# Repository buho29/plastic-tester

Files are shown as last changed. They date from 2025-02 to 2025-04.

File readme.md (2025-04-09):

# Plastic Tester

[Documentacion en español](<readme es.md>)

**Demo on YouTube**

Demo on YouTube (https://www.youtube.com/watch?v=grObh11XFaI)

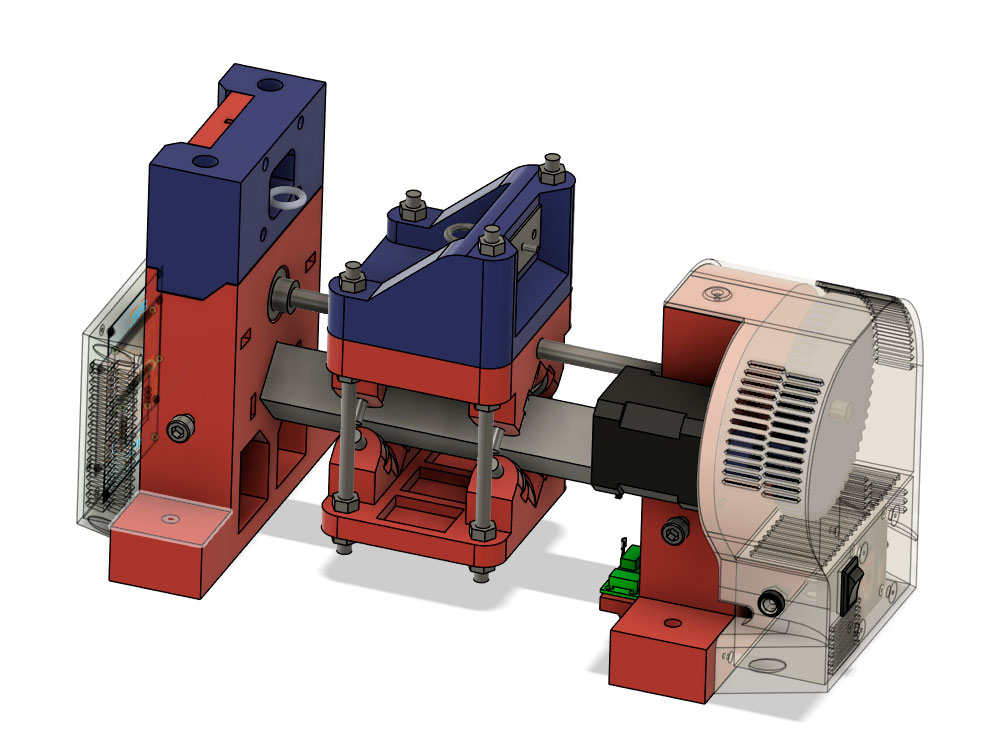
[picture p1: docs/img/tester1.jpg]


## General Description

Low-cost DIY system designed to perform tensile tests (*tensile testing machine*) on 3D-printed specimens.

Designed for:

- Validating the quality of 3D printing filaments
- Evaluating layer adhesion in printed parts
- Obtaining comparative data between different filaments
- Obtaining comparative data between different printing parameters
- Being compact and portable

The system uses:
- **Sensor**: Affordable load cell with HX711
- **Actuator**: Stepper motor with driver
- **Control**: Web interface accessible via WiFi
- **Visualization**: Real-time force/displacement graphs

**Key Features**:
- Approximate cost: < €100 in components
- Maximum force: 50kg
- Accuracy: ±0.1kg
- Adjustable speed: 0.1 - 5 mm/min

## Development Notes
- Platform: ESP32
- IDE: PlatformIO

## 3D Printing
- The printable parts and original files (Fusion 360) are located in the folder
[docs/3d](./docs/3d)

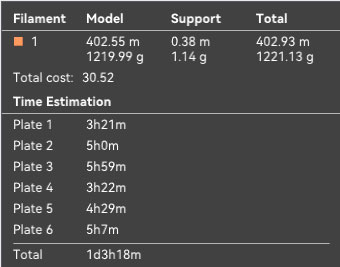
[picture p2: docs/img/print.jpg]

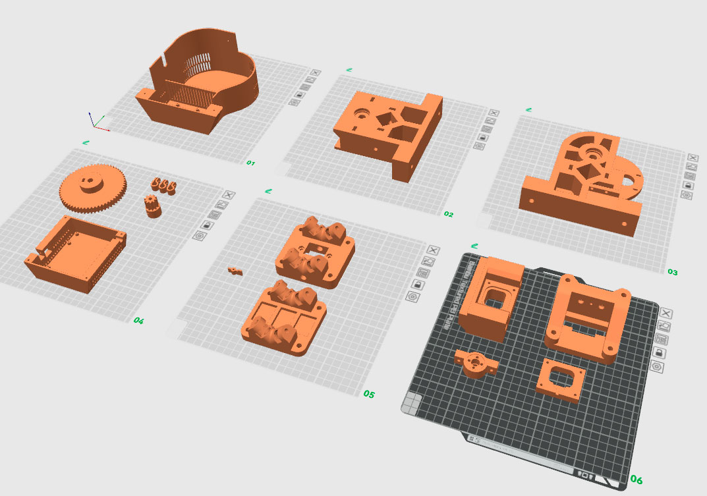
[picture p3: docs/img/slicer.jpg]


## Assembly
### Frame
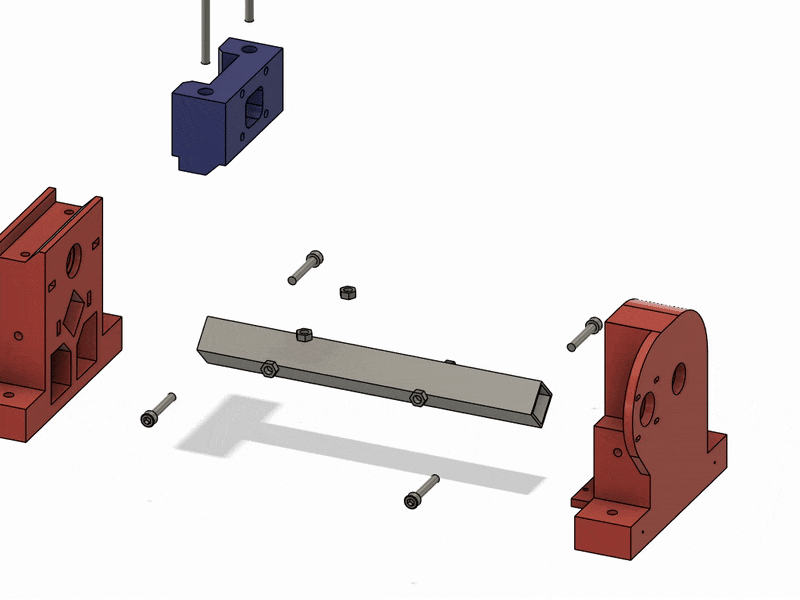
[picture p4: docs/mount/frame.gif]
Frame


[Download video](./docs/mount/frame.avi)

### Mount the T8 nut on the holder with inserts

- Cut off the excess screws

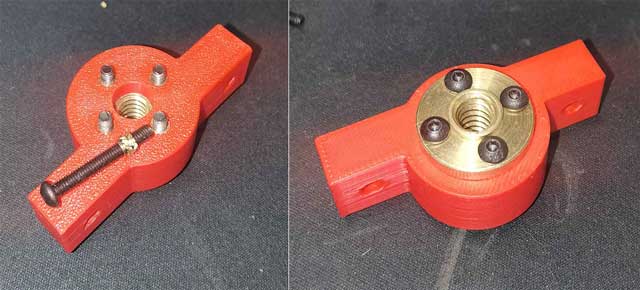
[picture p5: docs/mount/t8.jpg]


### Slide
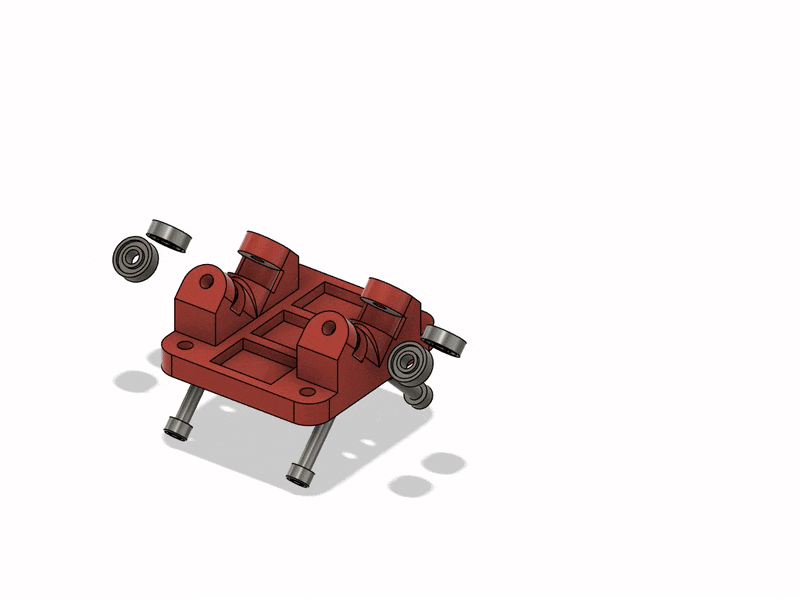
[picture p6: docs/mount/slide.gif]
slide


[Download video](./docs/mount/slide.avi)

### Complete
slide

[Download video](./docs/mount/mount.avi)

### Aligning the T8 nut holder with the lead screw

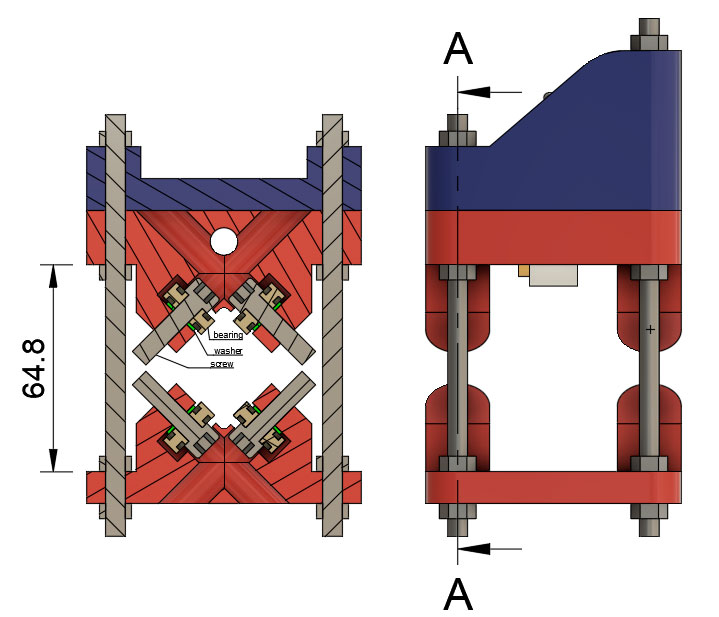
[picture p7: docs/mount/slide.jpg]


The screw is 5.8mm in diameter, and the bearings have a 6mm inner diameter.

1. Best method:
    - Center the screw with electrical tape.
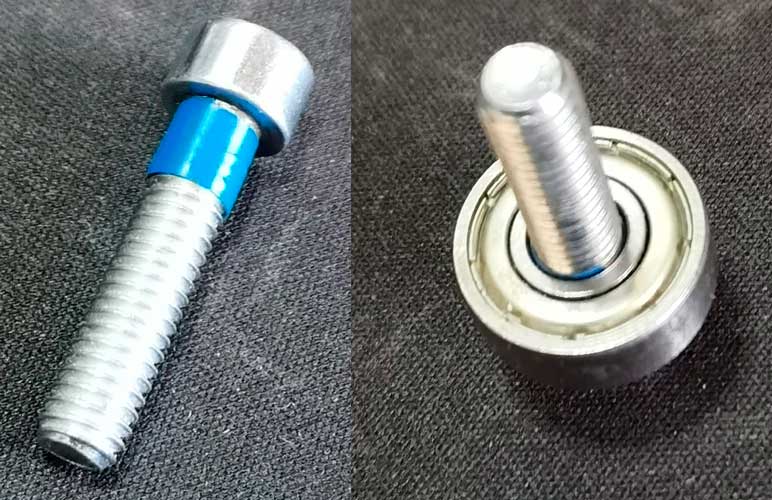
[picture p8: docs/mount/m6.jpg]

    - Place 2 pieces of 0.2mm paper; since the support area has a base, I left 0.25mm of clearance.
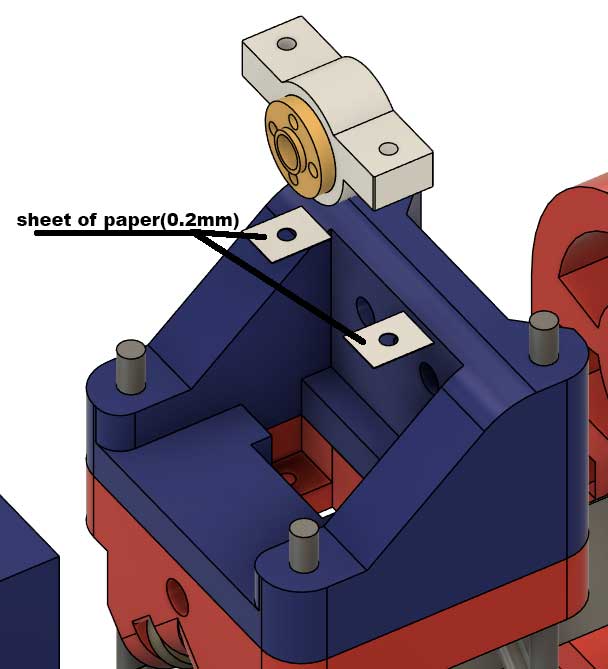
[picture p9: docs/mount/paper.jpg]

2. Alternative method:
    - Push towards the base and tighten the screw.
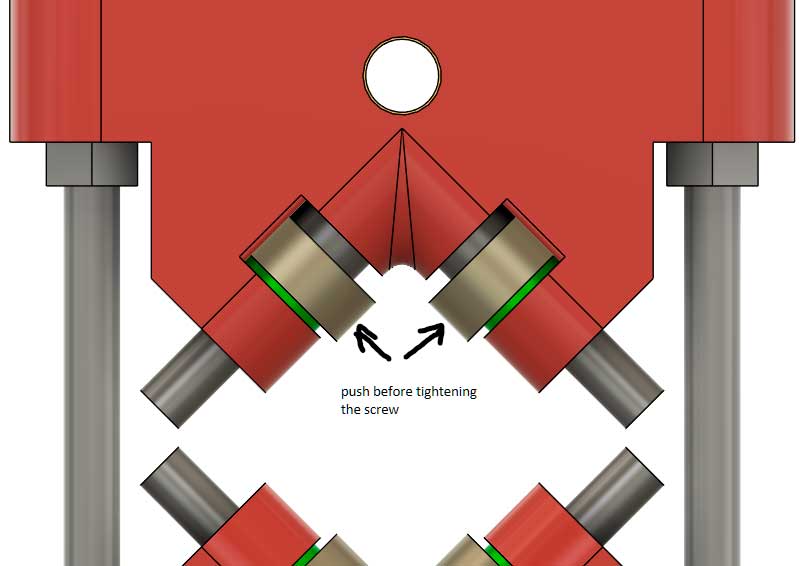
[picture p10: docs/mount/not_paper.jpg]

    - Place 4 or more pieces of 0.2mm paper.

## Hardware

### Load Cell (HX711)
```cpp
const int LOADCELL_DOUT_PIN = 26;
const int LOADCELL_SCK_PIN = 25;
const float CALIBRATING_FACTOR = -2316138 / 44.34; // real kg reading
```
1. **Set the HX711 to 80hz** 
    - Cut the blue square
    - Solder the red square 

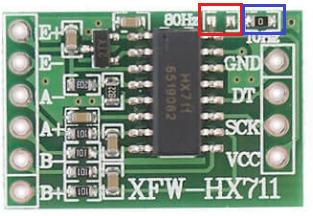
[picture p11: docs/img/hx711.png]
hx711


2. **Attach the screw to the sensor**
    - Drill with a 3mm bit 
    - Attach the eye screw with 2 nuts

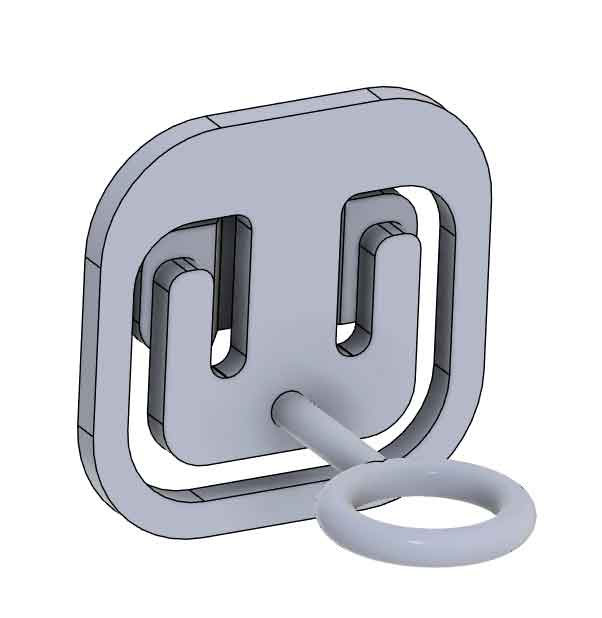
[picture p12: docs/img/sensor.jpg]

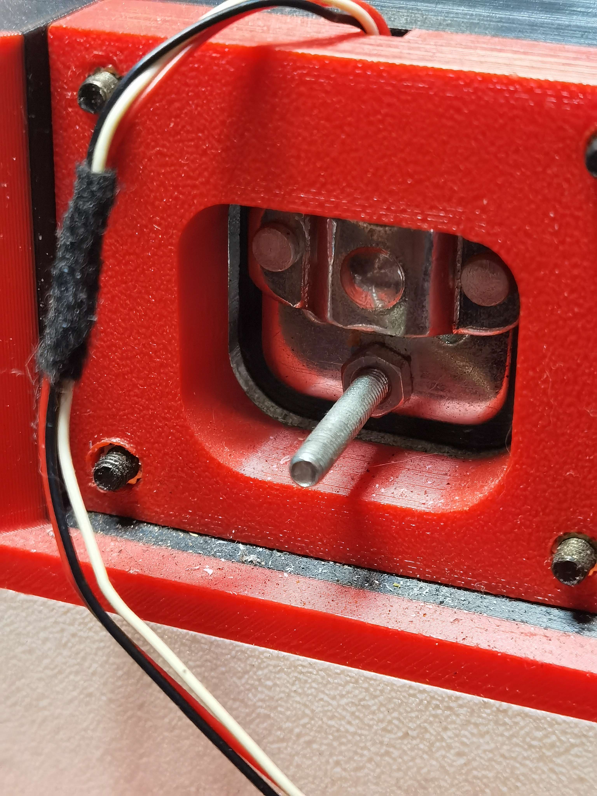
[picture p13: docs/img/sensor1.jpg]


**Note: The screw must be soldered**
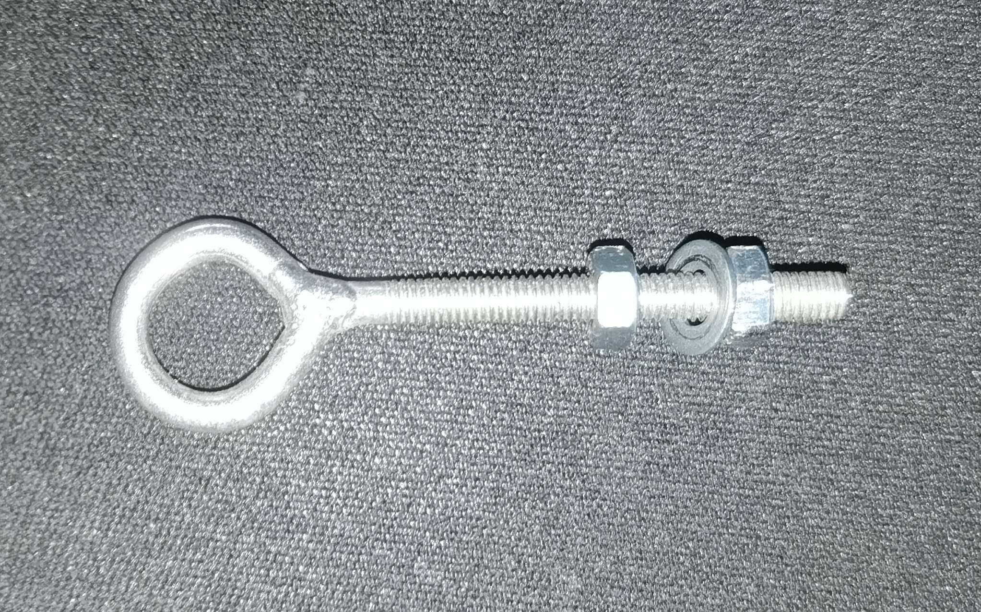
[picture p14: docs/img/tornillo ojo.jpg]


### PCB
 - 2 resistors of 1K Ohm are needed
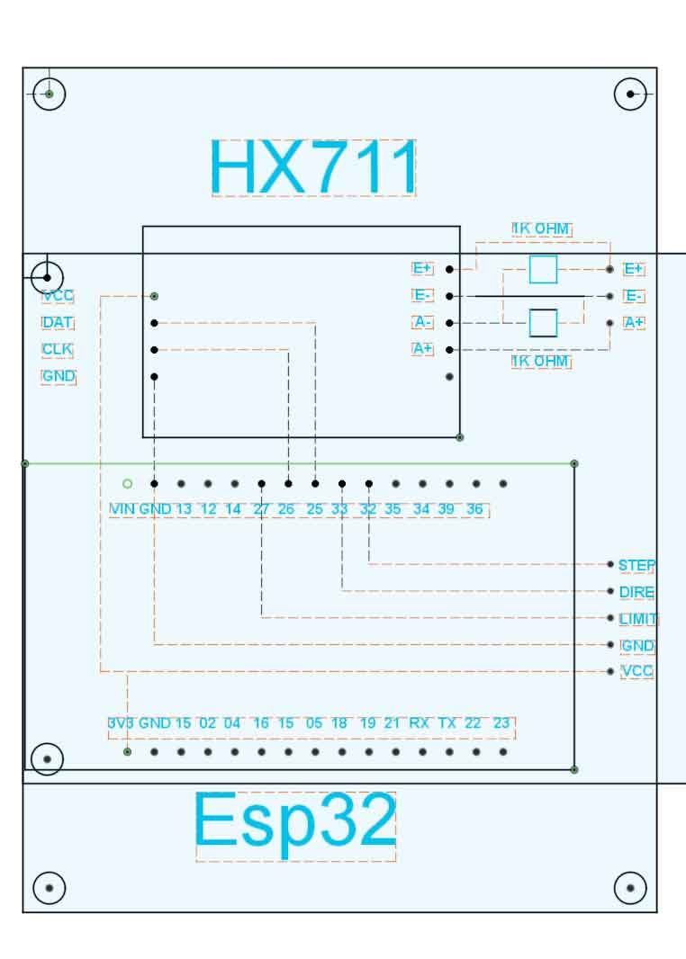
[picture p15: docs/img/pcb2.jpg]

**Flipped view (if looking from above)**
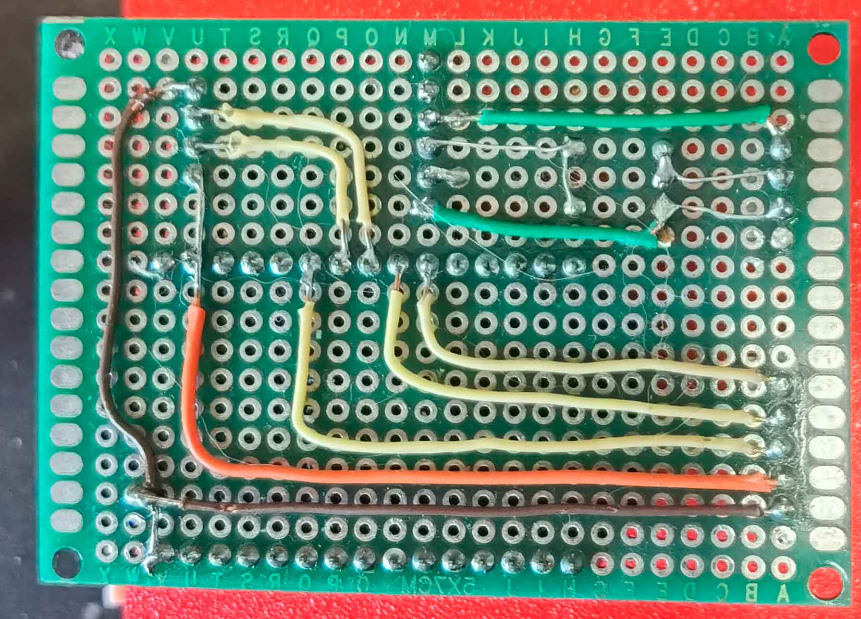
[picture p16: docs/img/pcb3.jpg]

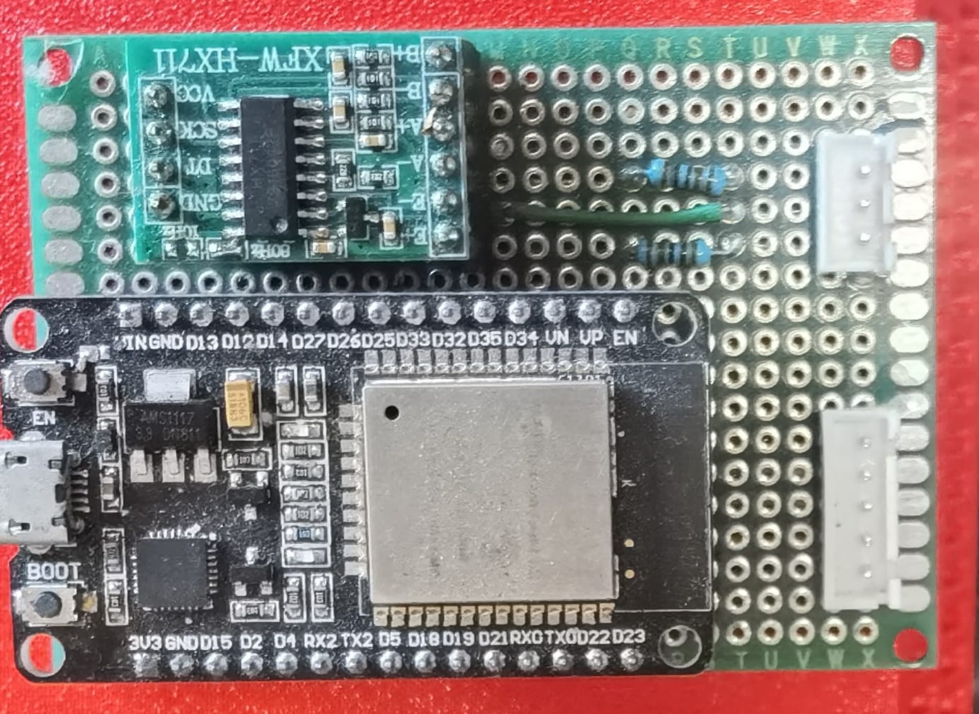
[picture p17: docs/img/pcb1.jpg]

**Normal view (if looking from below)**
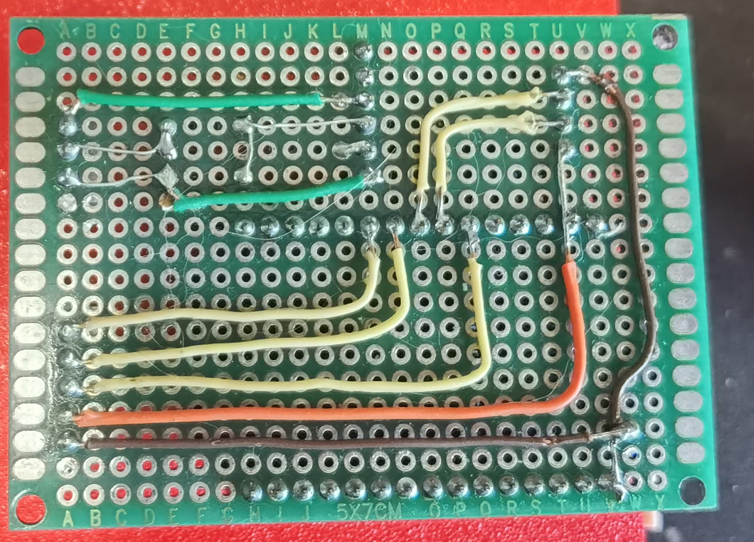
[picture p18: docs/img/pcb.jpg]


### Complete Circuit
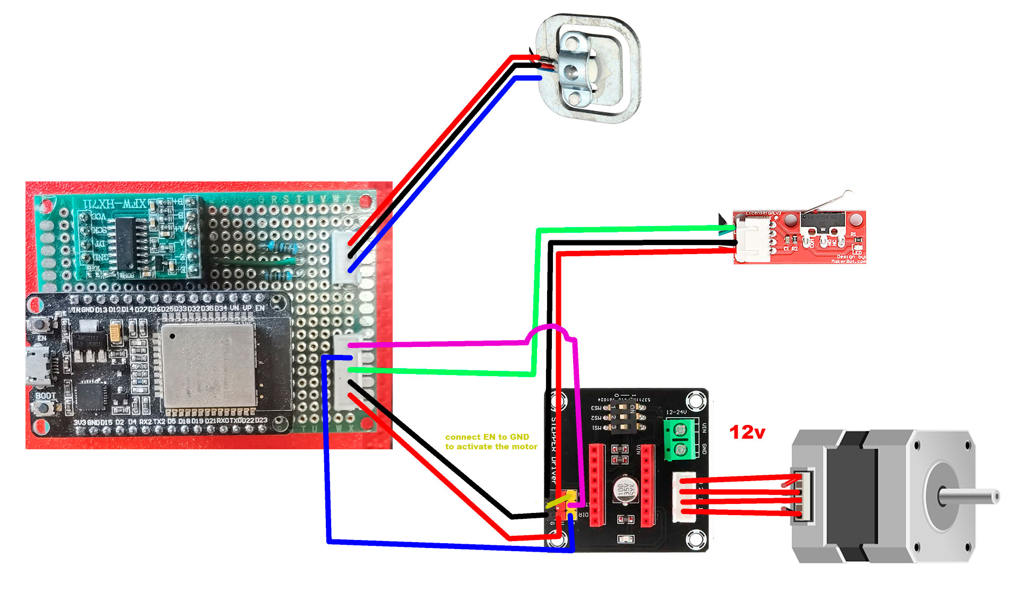
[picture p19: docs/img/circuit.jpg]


### Stepper Motor
```cpp
const uint8_t MOTOR_STEP_PIN = 32;
const uint8_t MOTOR_DIRECTION_PIN = 33;
const uint8_t ENDSTOP_PIN = 27;
```
## Installation

1. **Edit [config.json](./data/data/config.json): (optional)**
    ```json
    {
      "wifi_pass": "your pass",
      "wifi_ssid": "your wifi"
    }
    ```
2. **Upload the `data` folder to the ESP32:**
    1. If you want to update/copy the `vue` folder to `data/www`, run:
        ```bash
        python update_data_web.py 
        ```
    2. Steps in PlatformIO:
        - Build filesystem image
        - Upload filesystem image
3. **Compile the project:**
    1. Upload

## Usage

By default, the user is:
- **Username**: admin
- **Password**: admin

### On PC
- Open the browser and go to [http://plastester.local](http://plastester.local)
- Change the WiFi credentials if necessary (Options Page)

### On Mobile (Android)
mDNS does not work on mobile devices, you need to use the IP:
- If connected to WiFi, open the browser and go to your device's IP (e.g., [http://192.168.1.57](http://192.168.1.57))
- If not connected or you don't know the IP:
    - Connect to the device's WiFi and open the browser at [http://plastester.local](http://plastester.local) or [http://8.8.4.4](http://8.8.4.4)
    - Copy the IP and change the WiFi credentials if necessary (System/Options Page)

### Open from `index.html` in the `vue` folder
- Edit the `index.html` and change the host by setting the ESP32's IP:
    ```js
    // To run the HTML outside the ESP32 
    var host = document.location.host;
    if (host === "" || // local file
        host === "127.0.0.1:3000") // preview in preview (visual code addon)
        host = '192.168.1.57'; // ESP32 IP
    ```

## Vue/Quasar

- Using **Vue v2** and **Quasar v1** (decided not to upgrade to Vue 3 for now)
- Not using CLI, editing `.js` files directly in the `vue` folder

## Web Page Files
- `index.html`: Home and host configuration and web colors
- `main.js`: Router and Vue creation and configuration
- `vuex.js`: WebSocket data and event management
- `pages/`: Folder containing the web pages
- `components.js`: Definition of components used on the web (charts)

## Shopping List

**The links are for reference only, make sure it's the best purchase** 

| Item                              | Used | (€)  | Link |
|----------------------------------|------|------|------|
| **Main Components**              |      |      |      |
| Screw Trapezoidal T8 300mm P2L2  | 1    | 9,89 | [Link](https://es.aliexpress.com/item/32507277503.html) |
| Nema17 48mm 2A                   | 1    | 13,19| [Link](https://es.aliexpress.com/item/1005004731197516.html) |
| Stepper DRV8825                  | 1    | 1,59 | [Link](https://www.aliexpress.com/item/4000083334758.html) |
| Expansion Board Stepper          | 1    | 1,79 | [Link](https://es.aliexpress.com/item/10000278156894.html) |
| Weight Sensor 50KG               | 1    | 1,30 | [Link](https://es.aliexpress.com/item/1005006668822214.html) |
| HX711 Green Small                | 1    | 1,18 | [Link](https://www.aliexpress.com/item/1005007091731394.html) |
| ESP32 DEVKIT V1                  | 1    | 3,79 | [Link](https://es.aliexpress.com/item/1005008503831020.html) |
| F8-22M Bearing Axial 8x22x7 (x2) | 2    | 1,89 | [Link](https://es.aliexpress.com/item/1005007129279401.html) |
| 606ZZ 6x17x6mm (x10)             | 8    | 3,09 | [Link](https://es.aliexpress.com/item/1005003067718206.html) |
| 608zz 8x22x7mm (x10)             | 2    | 3,89 | [Link](https://es.aliexpress.com/item/1005003067718206.html) |
| Square Alu 25x25x2 - 250         | 1    | 3,59 | [Link](https://es.aliexpress.com/item/1005007456875848.html) |
| Endstop Switch                   | 1    | 2,79 | [Link](https://es.aliexpress.com/item/1005003139255707.html) |
| Lock Collar T8 (x5)              | 3    | 1,69 | [Link](https://es.aliexpress.com/item/1005001667273798.html) |
| Power Supply Jack Socket         | 1    | 0,54 | [Link](https://www.aliexpress.com/item/32838214586.html) |
| Switch (x5)                      | 1    | 1,34 | [Link](https://www.aliexpress.com/item/32873386670.html) |
| XH2.54 Connector                 | 1    | 2,99 | [Link](https://www.aliexpress.com/item/1005007425641197.html) |
| M3xL3xOD4.2 (x50)                | 10   | 1,59 | [Link](https://www.aliexpress.com/item/1005006472702418.html) |
| PCB Board Protoboard 5x7         | 1    | 0,90 | [Link](https://www.aliexpress.com/item/1005006100148769.html) |
| 1K Ohm resistor                  | 2    |      |      |
| **Total Components**             |      | 57,03|      |
|                                  |      |      |      |
| **Screws and Accessories (best in local seller)**       |      |      |      |
| D Ring Shackle Closed M3 (x2)    | 2    | 2,82 | [Link](https://www.aliexpress.com/item/1005007576884635.html) |
| Nuts M6 (x50)                    | 28   | 4,28 | [Link](https://www.aliexpress.com/item/1005007593861199.html) |
| Nuts M4 (x25)                    | 2    | 1,59 | [Link](https://www.aliexpress.com/item/1005007593861199.html) |
| Nuts M3 (x50)                    | 8    | 1,69 | [Link](https://es.aliexpress.com/item/1005004531602992.html) |
| Screw M6 X 25 (x20)              | 12   | 5,84 | [Link](https://www.aliexpress.com/item/1005003463456440.html) |
| Screw M6 X 60 (x10)              | 6    | 4,48 | [Link](https://www.aliexpress.com/item/1005004527586307.html) |
| Screw M6 X 35 (x5)               | 4    | 1,89 | [Link](https://www.aliexpress.com/item/1005004527586307.html) |
| Screw M3 X 22 (x40)              | 8    | 2,05 | [Link](https://www.aliexpress.com/item/1005004527586307.html) |
| Screw M4 X 20 (x20)              | 2    | 1,95 | [Link](https://www.aliexpress.com/item/1005004527586307.html) |
| Washer M6 12x1.5 (x50)           | 8    | 2,06  | [Link](https://www.aliexpress.com/item/1005004527586307.html) |
| Sheep Eye Screw M3 (x10)         | 2    | 2,59 | Local Seller |
| Threaded Rod M6 -1000            | 1    | 0,80 | Local Seller |
| Plywood Board 340x160x20         | 1    | 6,00 | Local Seller |
| **Total Screws**                 |      | 38,04|      |
| **TOTAL GENERAL**                |      | 95,07|      |
|                                  |      |      |      |
| **Tools**                        |      |      |      |
| Crimping Plier XH2.54            | 1    | 9,39 | [Link](https://www.aliexpress.com/item/1005006224244342.html) |

## Libraries Used

### C++

- [ESPAsyncWebServer](https://github.com/ESP32Async/ESPAsyncWebServer)
- [AsyncTCP](https://github.com/ESP32Async/AsyncTCP)
- [ArduinoJson](https://arduinojson.org/)
- [FastAccelStepper](https://github.com/gin66/FastAccelStepper)

### JavaScript

- [Vue v2](https://v2.vuejs.org/)
- [Vuex v3](https://v3.vuex.vuejs.org/)
- [Vue-router v3](https://v3.router.vuejs.org/)
- [Quasar Framework v1](https://v1.quasar.dev/)
- [Chart.js v2](https://www.chartjs.org)/[Vue-chartjs v3](https://vue-chartjs.org)

## Screens
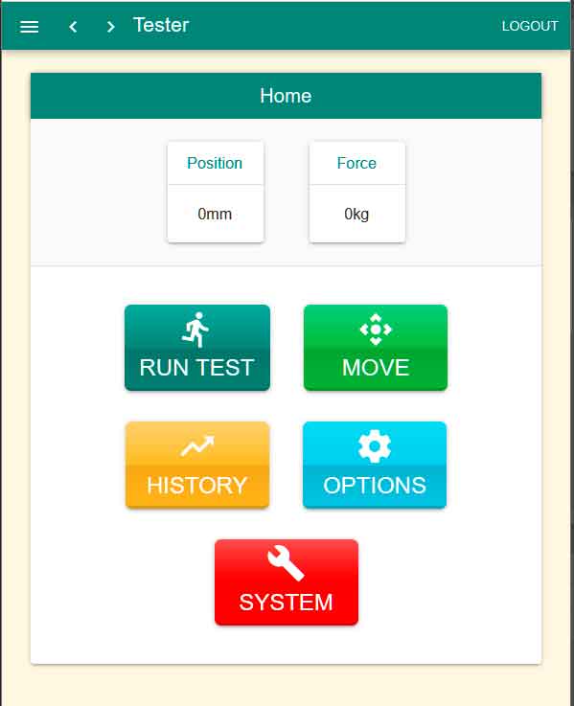
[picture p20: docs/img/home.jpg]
Home

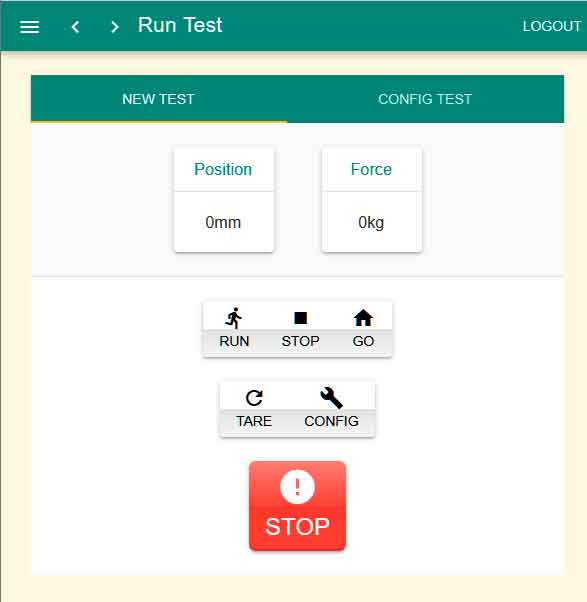
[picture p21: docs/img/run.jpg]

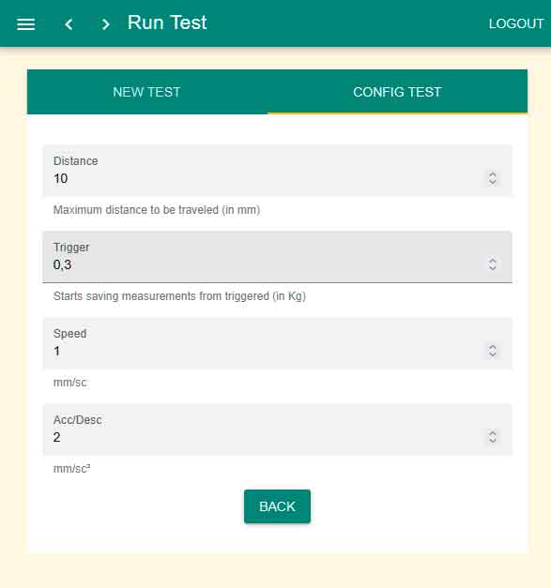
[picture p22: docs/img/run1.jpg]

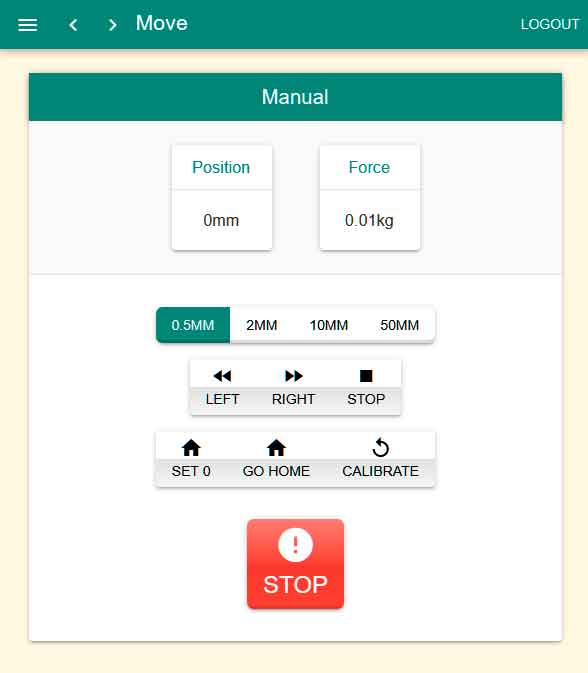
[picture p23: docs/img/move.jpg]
Move

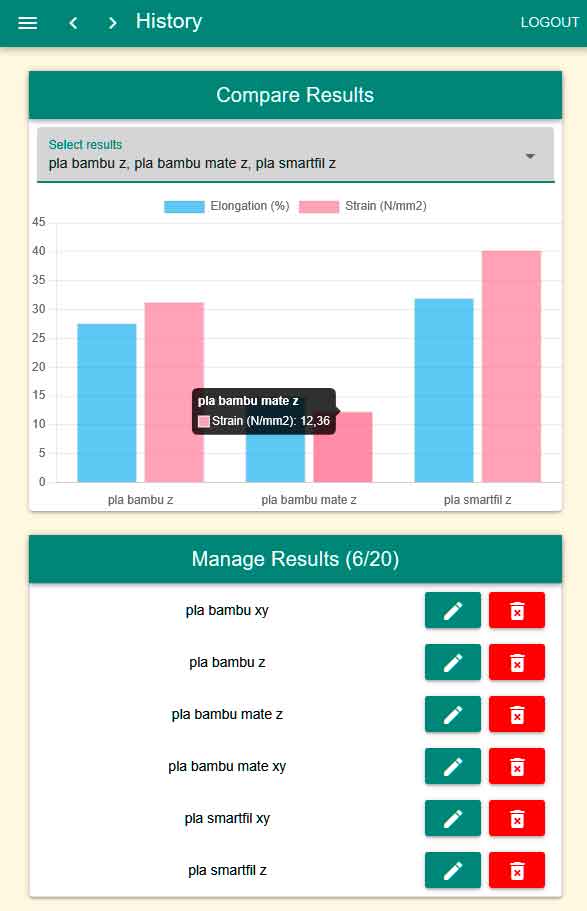
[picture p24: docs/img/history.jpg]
History

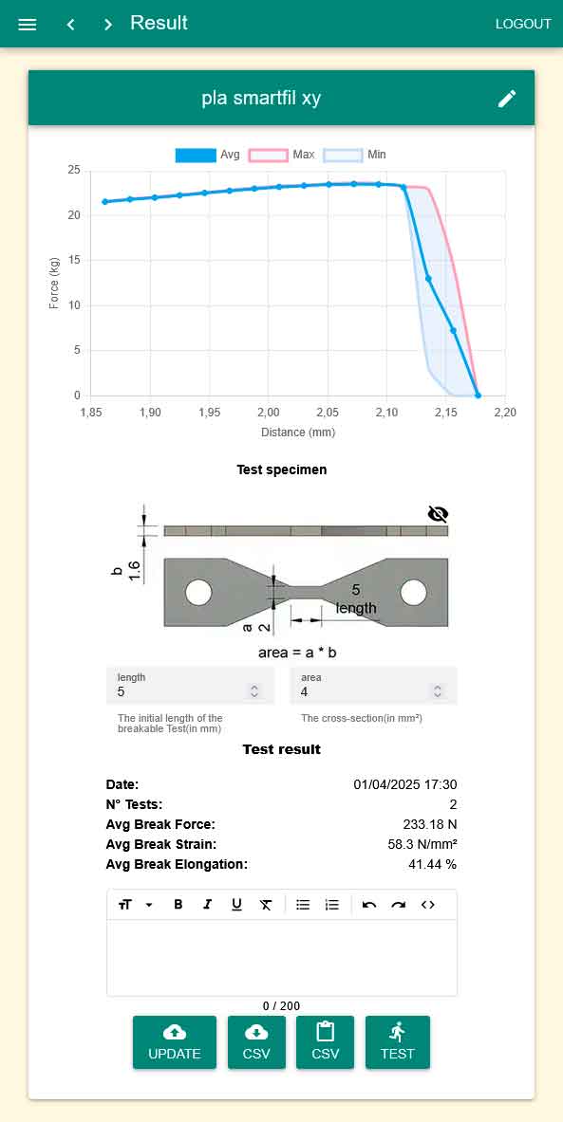
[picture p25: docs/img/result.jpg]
Result

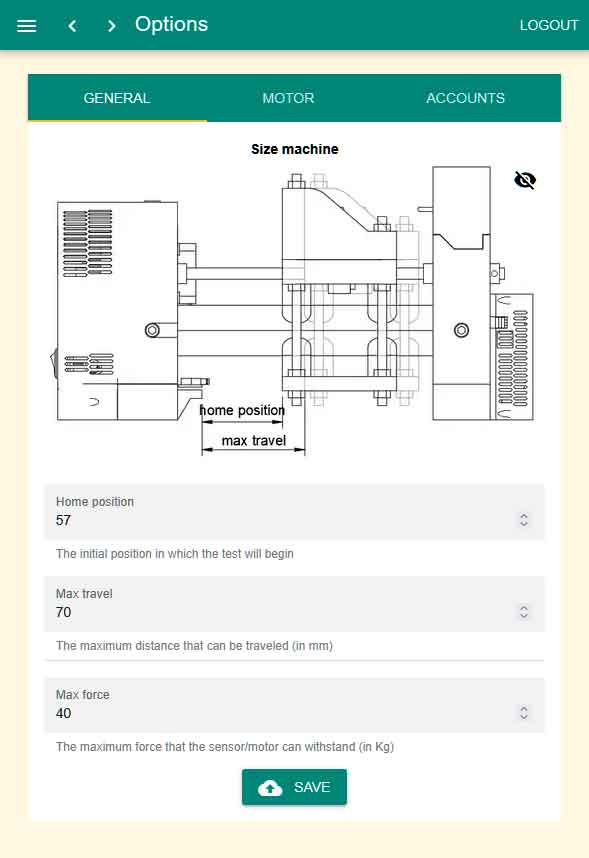
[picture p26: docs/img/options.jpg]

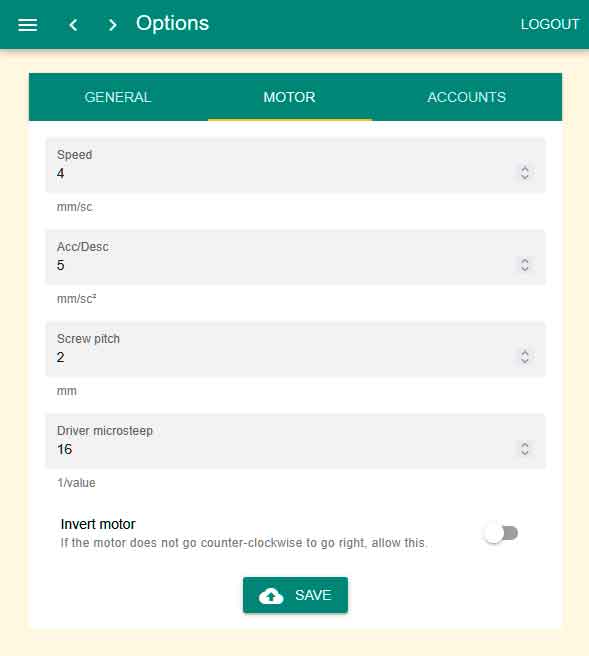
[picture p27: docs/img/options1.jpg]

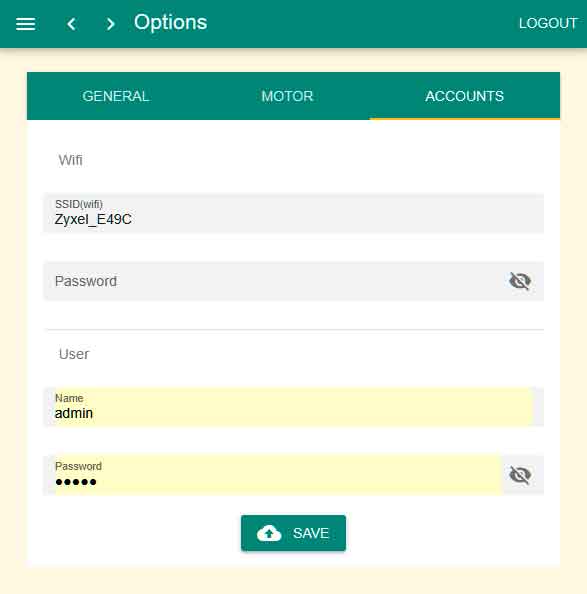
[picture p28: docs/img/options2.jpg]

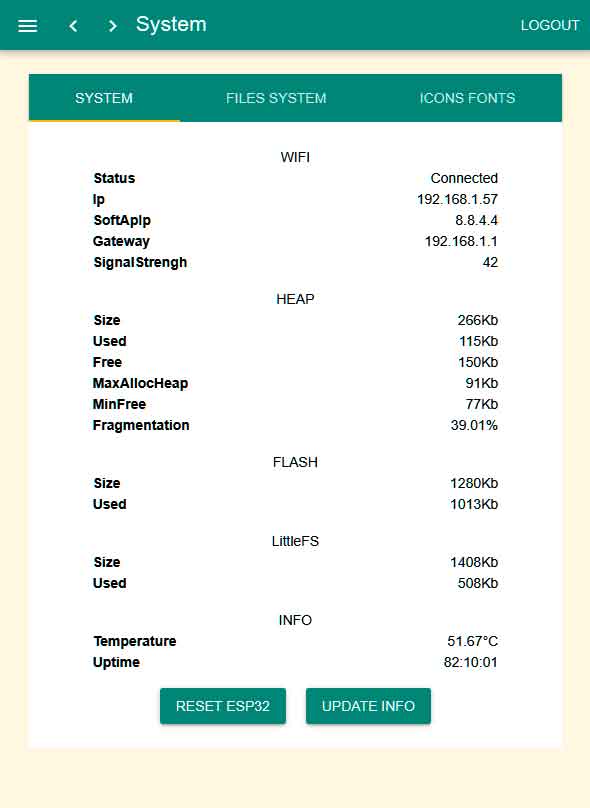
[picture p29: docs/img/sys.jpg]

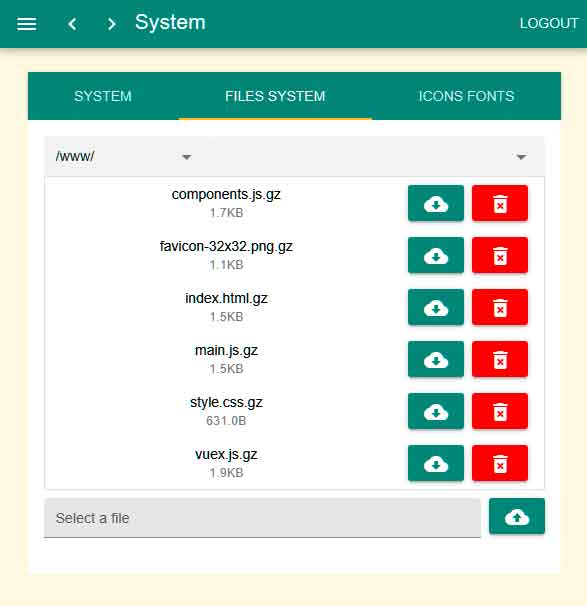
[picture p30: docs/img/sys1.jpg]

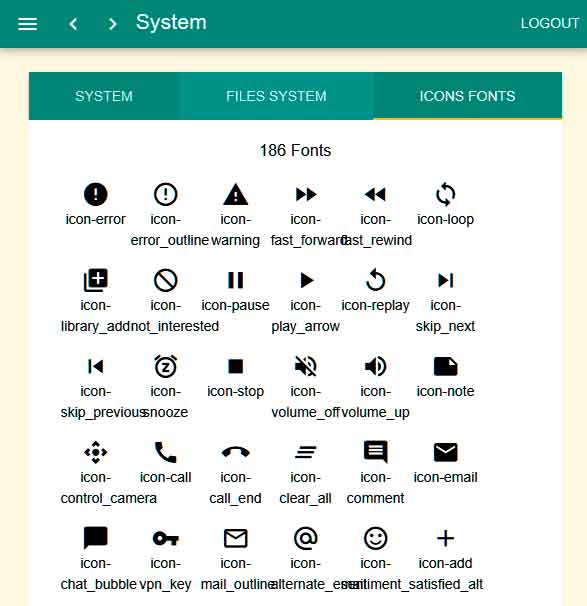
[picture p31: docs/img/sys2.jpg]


## Gallery
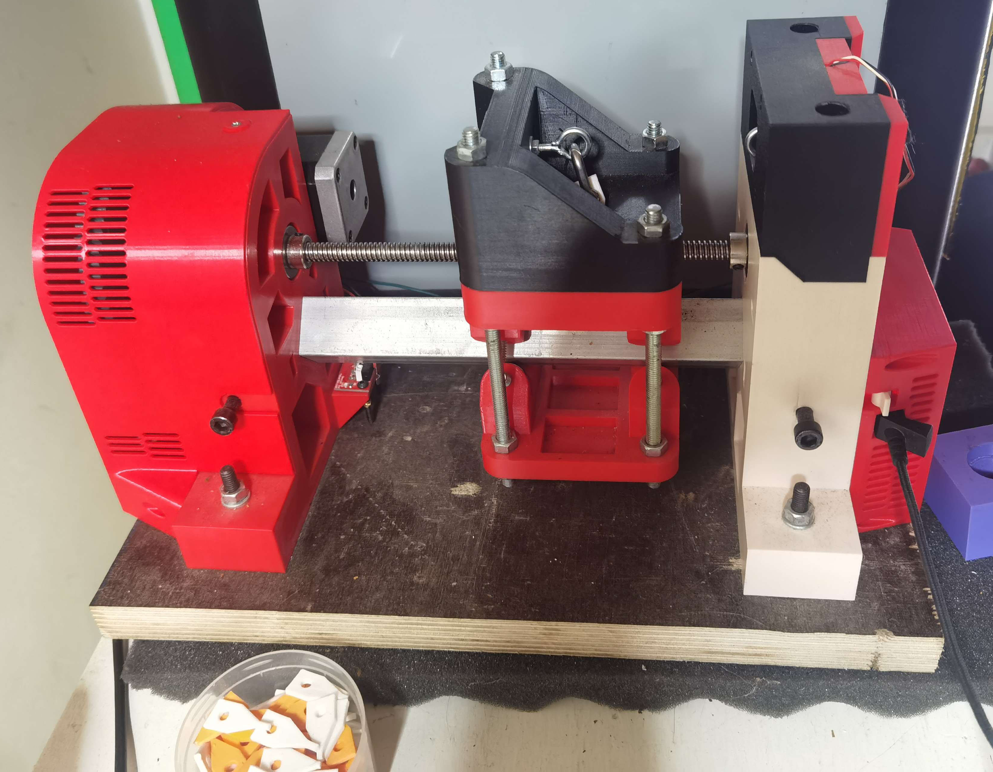
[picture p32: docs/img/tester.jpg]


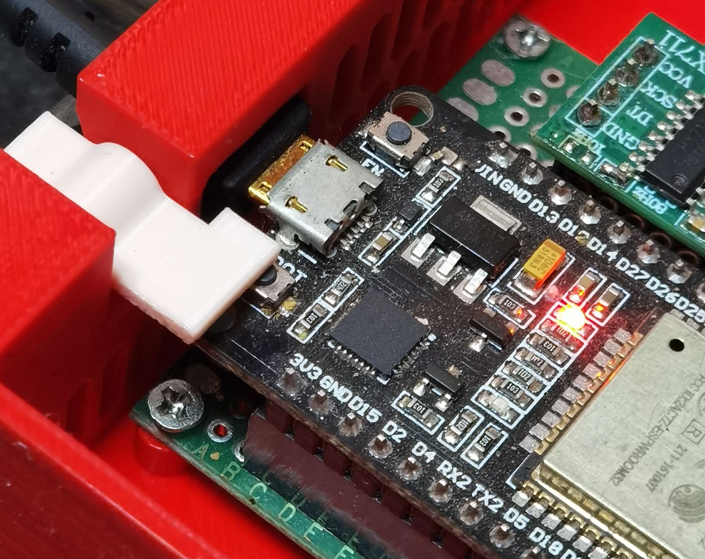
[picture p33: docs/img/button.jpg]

**I used a 2x13mm steel shaft** (a cut drill bit in my case)

- Insert it through the "usb" window

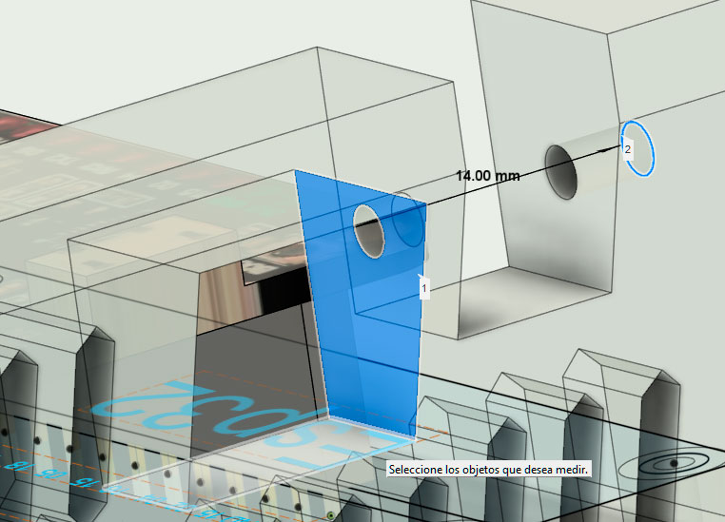
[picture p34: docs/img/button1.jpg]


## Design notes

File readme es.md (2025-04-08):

# Plastic Tester

**Demo en YouTube**

Demo en YouTube (https://www.youtube.com/watch?v=grObh11XFaI)



## Descripción General

Sistema DIY de bajo coste para realizar ensayos de tracción (*tensile testing machine*) en probetas impresas en 3D. 

Diseñado para:

- Validar la calidad de filamentos para impresión 3D
- Evaluar la adhesión entre capas de piezas impresas
- Obtener datos comparativos entre varios filamentos
- Obtener datos comparativos entre diferentes parámetros de impresión
- Que sea pequeño

El sistema utiliza:
- **Sensor**: Celda de carga económico con HX711
- **Actuador**: Motor paso a paso con driver
- **Control**: Interfaz web accesible vía WiFi
- **Visualización**: Gráficas de fuerza/desplazamiento

**Características principales**:
- Coste aproximado: < 100€ en componentes
- Fuerza máxima: 50kg
- Precisión: ±0.1kg
- Velocidad ajustable: 0.1 - 5 mm/min

## Notas de Desarrollo
- Plataforma: ESP32
- IDE: PlatformIO

## Impresion 3D
- las piezas para imprimir y los ficheros originales(fusion 360) se encuentran en la carpeta
[docs/3d](./docs/3d)




## Montaje
### Frame
Frame

[Descargar video](./docs/mount/frame.avi)

### Montar la tuerca T8 en el soporte con los inserts

- cortar los tornillos sobrantes



### Slide
slide

[Descargar video](./docs/mount/slide.avi)

### Completo
slide

[Descargar video](./docs/mount/mount.avi)

### Alineamiento de el soporte de la tuerca T8 con el husillo



el tornillo mide 5.8mm de diámetro y los rodamientos tienen 6mm de interior

1. mejor forma
    - centrando el tornillo con cinta aislante,

    - poner 2 trozos de papel de 0.2mm, como la zona donde apoya lleva soporte le deje 0.25mm de holgura 

2. también funciona
    - empujando hacia la base y apretando el tornillo

    - poner 4 trozos de papel o mas de 0.2mm

## Hardware

### Celda de Carga (HX711)
```cpp
const int LOADCELL_DOUT_PIN = 26;
const int LOADCELL_SCK_PIN = 25;
const float CALIBRATING_FACTOR = -2316138 / 44.34; // lectura/kg real
```
1. **Poner el HX711 a 80hz** 
    - cortar el cuadrado azul
    - soldar el cuadrado rojo 

hx711

2. **Colocar tornillo al sensor**
    - taladrar con una broca de 3mm 
    - poner el tornillo de ojo con 2 tuercas




**nota el tornillo tiene que estar soldado**


### PCB
 - se necesitan 2 resistencias de 1K Ohm

**vista volteada (si miramos desde arriba)**


**vista normal (si miramos por abajo)**


### Circuito completo


### Motor Paso a Paso
```cpp
const uint8_t MOTOR_STEP_PIN = 32;
const uint8_t MOTOR_DIRECTION_PIN = 33;
const uint8_t ENDSTOP_PIN = 27;
```
## Instalación

1. **Editar [config.json](./data/data/config.json): (opcional)**
    ```json
    {
      "wifi_pass": "tu pass",
      "wifi_ssid": "tu wifi"
    }
    ```
2. **Subir la carpeta `data` al ESP32:**
    1. Si deseas actualizar/copiar la carpeta `vue` a `data/www` ejecutar:
        ```bash
        python update_data_web.py 
        ```
    2. Pasos en PlatformIO:
        - Build filesystem image
        - Upload filesystem image
3. **Compilar el proyecto:**
    1. Upload

## Uso

Por defecto el usuario es:
- **Usuario**: admin
- **Password**: admin

### En PC
- Abre el navegador y ve a [http://plastester.local](http://plastester.local)
- Cambiar las credenciales del WiFi si es necesario (Pagina Options)

### En Móvil (Android)
El mDNS no funciona en móviles, necesitas usar la IP:
- Si está conectado al WiFi, abre el navegador y ve a la IP de tu dispositivo (ej.: [http://192.168.1.57](http://192.168.1.57))
- Si no está conectado o no sabes la IP:
    - Conéctate al WiFi del dispositivo y abre el navegador en [http://plastester.local](http://plastester.local) o [http://8.8.4.4](http://8.8.4.4)
    - Copia la IP y cambia las credenciales del WiFi si es necesario (Pagina System/Options)

### Abrir desde `index.html` de la carpeta `vue`
- Editar el `index.html` y cambiar el host poniendo la IP del ESP32:
    ```js
    // Para ejecutar el HTML fuera del ESP32 
    var host = document.location.host;
    if (host === "" || // archivo local
        host === "127.0.0.1:3000") // vista previa en preview (addon visual code)
        host = '192.168.1.57'; // IP del ESP32
    ```

## Vue/Quasar

- Uso **Vue v2** y **Quasar v1** (decidí no actualizar a Vue 3 por ahora)
- No uso CLI, edito los `.js` directamente de la carpeta `vue`

## Ficheros de la pagina web
- `index.html`: Inicio y configuración de host y colores de la web
- `main.js`: Creación y configuración de router y Vue
- `vuex.js`: Gestión de datos y eventos WebSocket
- `pages/`: Carpeta donde estan las páginas de la web
- `components.js`: Definición componentes usadas en la web (charts)

## Lista de la compra

**Los links solo son de referencia, asegurarse que es la mejor compra** 

| Item                             | Used | (€)  | Link |
|----------------------------------|------|------|------|
| **Componentes Principales**      |      |      |      |
| Screw Trapezoidal T8 300mm P2L2  | 1    | 9,89 | [Link](https://es.aliexpress.com/item/32507277503.html) |
| Nema17 48mm 2A                   | 1    | 13,19| [Link](https://es.aliexpress.com/item/1005004731197516.html) |
| Stepper DRV8825                  | 1    | 1,59 | [Link](https://www.aliexpress.com/item/4000083334758.html) |
| Expansion Board Stepper          | 1    | 1,79 | [Link](https://es.aliexpress.com/item/10000278156894.html) |
| Weight Sensor 50KG               | 1    | 1,30 | [Link](https://es.aliexpress.com/item/1005006668822214.html) |
| HX711 Green Small                | 1    | 1,18 | [Link](https://www.aliexpress.com/item/1005007091731394.html) |
| ESP32 DEVKIT V1                  | 1    | 3,79 | [Link](https://es.aliexpress.com/item/1005008503831020.html) |
| F8-22M Bearing Axial 8x22x7 (x2) | 2    | 1,89 | [Link](https://es.aliexpress.com/item/1005007129279401.html) |
| 606ZZ 6x17x6mm (x10)             | 8    | 3,09 | [Link](https://es.aliexpress.com/item/1005003067718206.html) |
| 608zz 8x22x7mm (x10)             | 2    | 3,89 | [Link](https://es.aliexpress.com/item/1005003067718206.html) |
| Square Alu 25x25x2 - 250         | 1    | 3,59 | [Link](https://es.aliexpress.com/item/1005007456875848.html) |
| Endstop Switch                   | 1    | 2,79 | [Link](https://es.aliexpress.com/item/1005003139255707.html) |
| Lock Collar T8 (x5)              | 3    | 1,69 | [Link](https://es.aliexpress.com/item/1005001667273798.html) |
| Power Supply Jack Socket         | 1    | 0,54 | [Link](https://www.aliexpress.com/item/32838214586.html) |
| Switch (x5)                      | 1    | 1,34 | [Link](https://www.aliexpress.com/item/32873386670.html) |
| XH2.54 Connector                 | 1    | 2,99 | [Link](https://www.aliexpress.com/item/1005007425641197.html) |
| M3xL3xOD4.2 (x50)                | 10   | 1,59 | [Link](https://www.aliexpress.com/item/1005006472702418.html) |
| PCB Board Protoboard 5x7         | 1    | 0,90 | [Link](https://www.aliexpress.com/item/1005006100148769.html) |
| 1K Ohm resistor                  | 2    |      |      |
| **Total Componentes**            |      | 57,03|      |
|                                  |      |      |      |
| **Tornillos y Accesorios (mejor de un vendedor local)** |      |      |      |
| D Ring Shackle Closed M3 (x2)    | 2    | 2,82 | [Link](https://www.aliexpress.com/item/1005007576884635.html) |
| Nuts M6 (x50)                    | 28   | 4,28 | [Link](https://www.aliexpress.com/item/1005007593861199.html) |
| Nuts M4 (x25)                    | 2    | 1,59 | [Link](https://www.aliexpress.com/item/1005007593861199.html) |
| Nuts M3 (x50)                    | 8    | 1,69 | [Link](https://es.aliexpress.com/item/1005004531602992.html) |
| Screw M6 X 25 (x20)              | 12   | 5,84 | [Link](https://www.aliexpress.com/item/1005003463456440.html) |
| Screw M6 X 60 (x10)              | 6    | 4,48 | [Link](https://www.aliexpress.com/item/1005004527586307.html) |
| Screw M6 X 35 (x5)               | 4    | 1,89 | [Link](https://www.aliexpress.com/item/1005004527586307.html) |
| Screw M3 X 22 (x40)              | 8    | 2,05 | [Link](https://www.aliexpress.com/item/1005004527586307.html) |
| Screw M4 X 20 (x20)              | 2    | 1,95 | [Link](https://www.aliexpress.com/item/1005004527586307.html) |
| Washer M6 12x1.5 (x50)           | 8    | 2,06  | [Link](https://www.aliexpress.com/item/1005004527586307.html) |
| Sheep Eye Screw M3 (x10)         | 2    | 2,59 | Local Seller |
| Threaded Rod M6 -1000            | 1    | 0,80 | Local Seller |
| Plywood Board 340x160x20         | 1    | 6,00 | Local Seller |
| **Total Tornillos**              |      | 38,04|      |
| **TOTAL GENERAL**                |      | 95,07|      |
|                                  |      |      |      |
| **Herramientas**                 |      |      |      |
| Crimping Plier XH2.54            | 1    | 9,39 | [Link](https://www.aliexpress.com/item/1005006224244342.html) |

## Librerías usadas

### C++

- [ESPAsyncWebServer](https://github.com/ESP32Async/ESPAsyncWebServer)
- [AsyncTCP](https://github.com/ESP32Async/AsyncTCP)
- [ArduinoJson](https://arduinojson.org/)
- [FastAccelStepper](https://github.com/gin66/FastAccelStepper)

### JavaScript

- [Vue v2](https://v2.vuejs.org/)
- [Vuex v3](https://v3.vuex.vuejs.org/)
- [Vue-router v3](https://v3.router.vuejs.org/)
- [Quasar Framework v1](https://v1.quasar.dev/)
- [Chart.js v2](https://www.chartjs.org)/[Vue-chartjs v3](https://vue-chartjs.org)

## Screens
Home
Run
Run
Move
History
Result
Icons
Icons
Icons
System
System
System

## Galeria



**he usado un eje de acero 2x13mm** (una broca cortada en mi caso)

- se mete por la ventana "usb"



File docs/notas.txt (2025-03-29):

opciones :
	+ guardar home position
	+ guardar inversion de motor
	+ guardar max distancia
	+ guardar max peso
	- probarlo

+ crear panel configuracion test (tab)
	+ distancia
	+ trigger 
- enums 
	- notify (good,warn)
	- action (empty,checklimit)
	- step test
	- wifiReset ()

+ revisar motor.setHome y setConfigHome
+ limitar comandos al stop cuando esta funcionado el test

- reseteo velocidad
[x] no se puede parar normal si esta en el test
[x] reseteo de velocidad si se para el test

A4988
VREF=Imax.8.Rs
Vref=1.5 *8*0.05 = 0.6v

DRV8825 
VREF=Imax/2
Vref= 1.5/2 = 0.75v

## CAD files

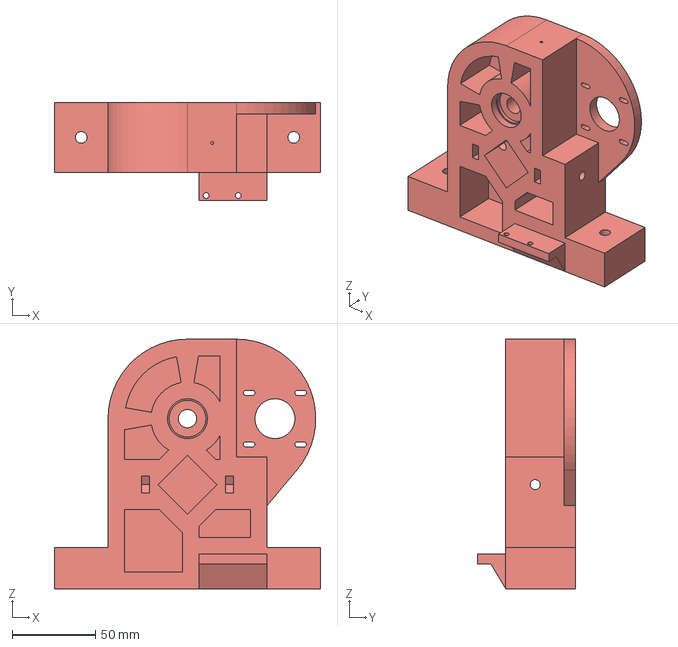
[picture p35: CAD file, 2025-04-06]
docs/3d/frame motor.step
160.0 x 59.0 x 150.2 mm

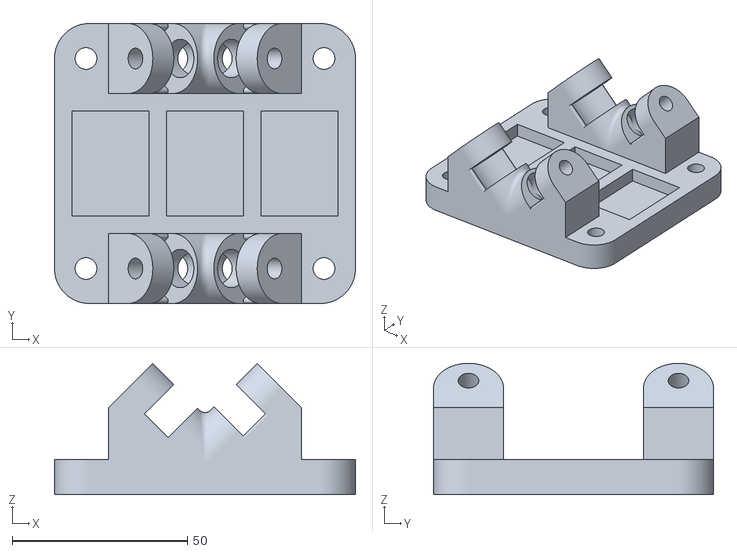
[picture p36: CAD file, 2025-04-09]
docs/3d/stl/slide-SOLID-2.stl
86.0 x 80.0 x 37.5

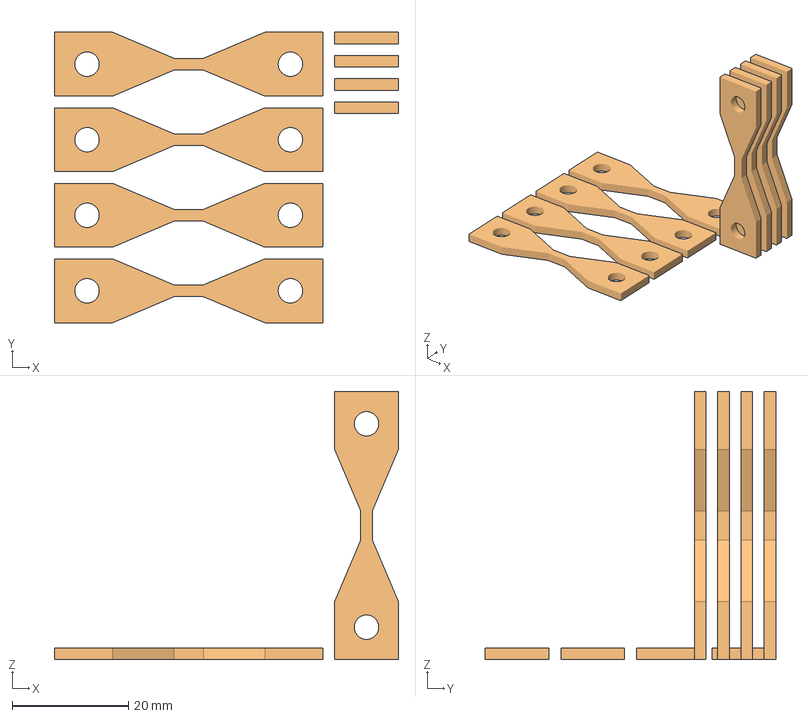
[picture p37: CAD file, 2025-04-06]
docs/3d/probeta.3mf
59.2 x 50.0 x 46.2 mm
Assembly x 2

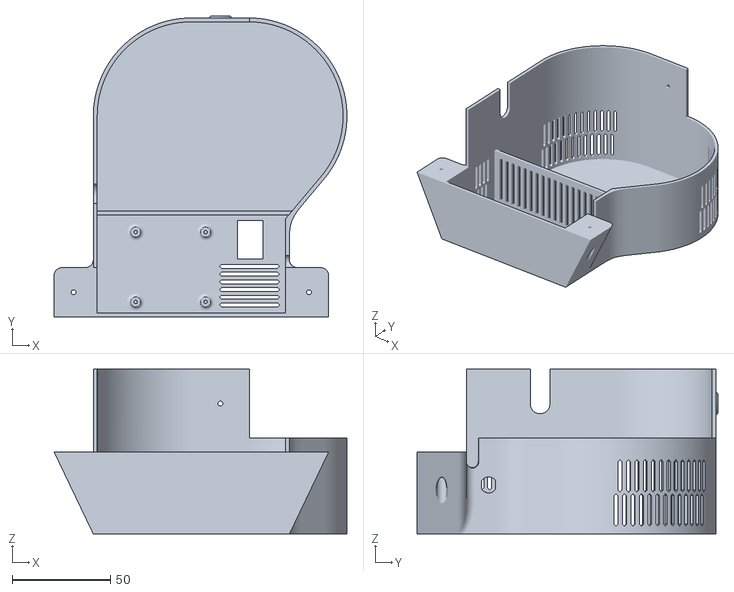
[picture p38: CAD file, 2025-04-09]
docs/3d/stl/tapa v2.stl
149.2 x 153.3 x 84.0

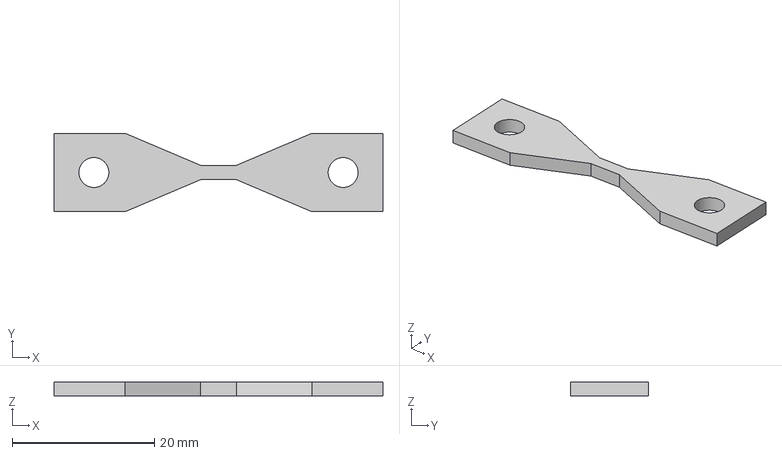
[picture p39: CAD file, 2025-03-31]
docs/3d/probeta v2.step
46.2 x 11.0 x 2.00 mm

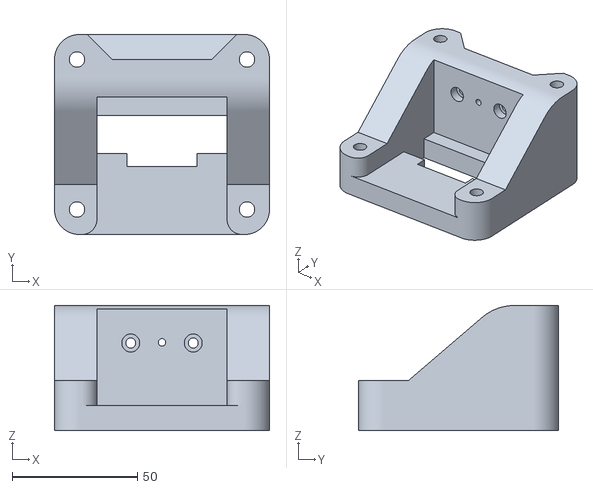
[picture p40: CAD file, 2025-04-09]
docs/3d/stl/COMPOUND-SOLID-4.stl
86.0 x 80.0 x 50.0

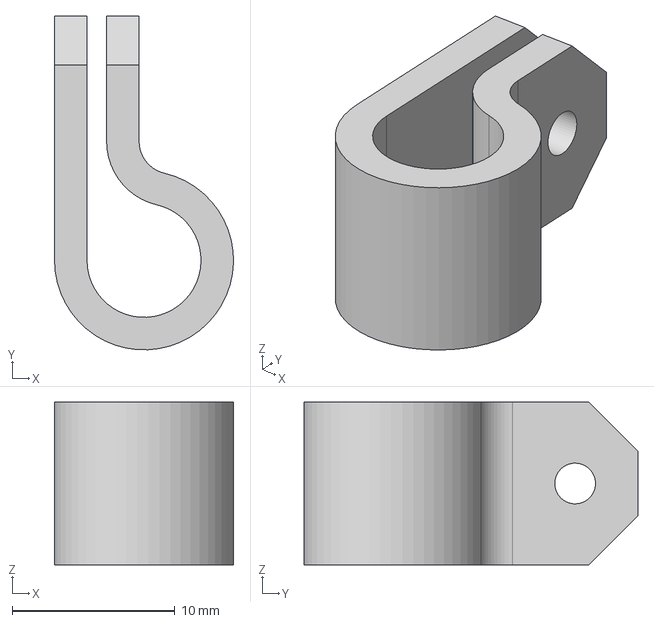
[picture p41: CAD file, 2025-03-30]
docs/3d/clip v1.step
11.0 x 20.5 x 10.0 mm

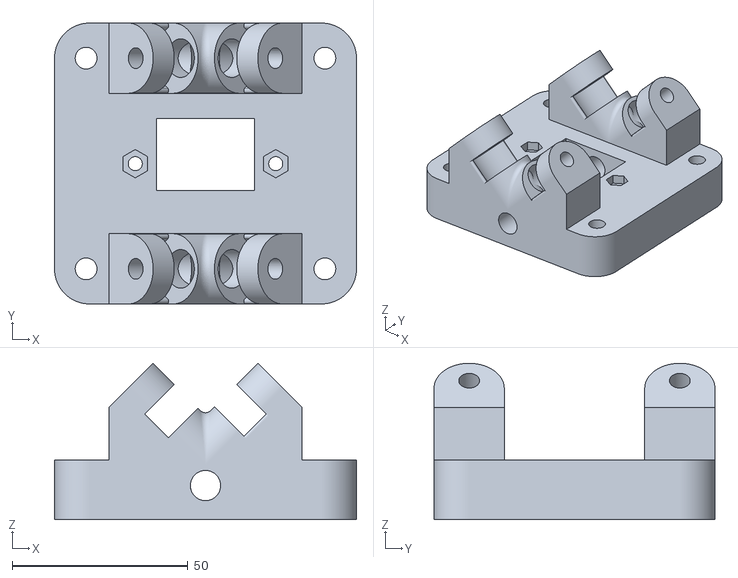
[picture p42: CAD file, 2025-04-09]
docs/3d/stl/slece-top.stl
86.0 x 80.0 x 44.5

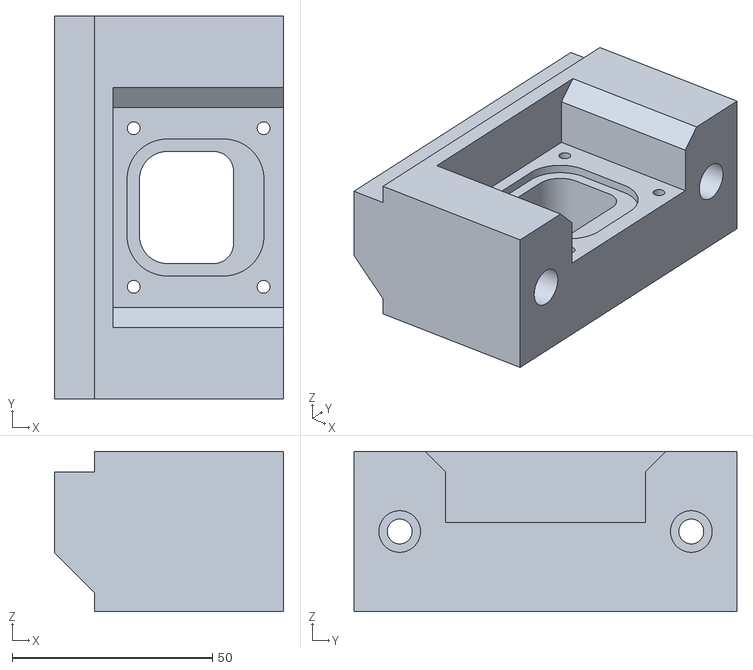
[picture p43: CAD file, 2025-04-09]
docs/3d/stl/COMPOUND-SOLID-3.stl
57.2 x 95.6 x 40.0

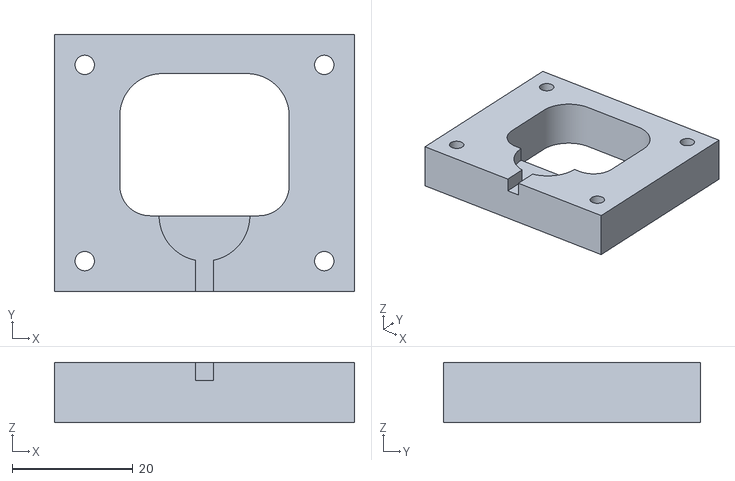
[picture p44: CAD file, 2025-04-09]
docs/3d/stl/sensor.stl
49.6 x 42.4 x 10.0

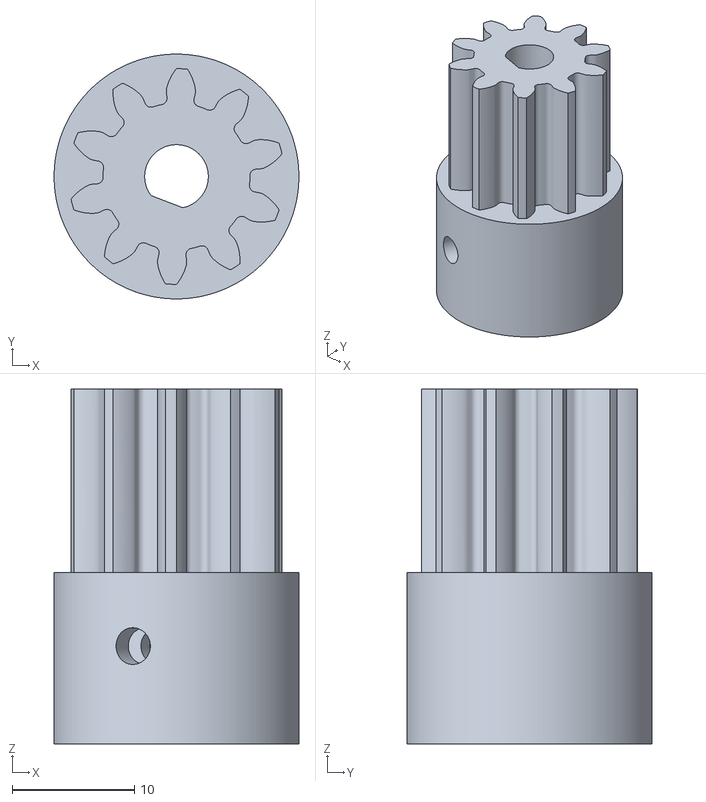
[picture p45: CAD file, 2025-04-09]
docs/3d/stl/gear t10 m1.stl
20.0 x 20.0 x 29.0

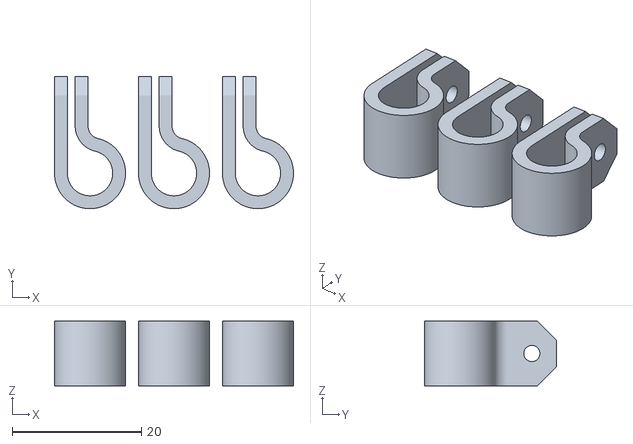
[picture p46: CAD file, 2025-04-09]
docs/3d/stl/clip.stl
37.0 x 20.5 x 10.0

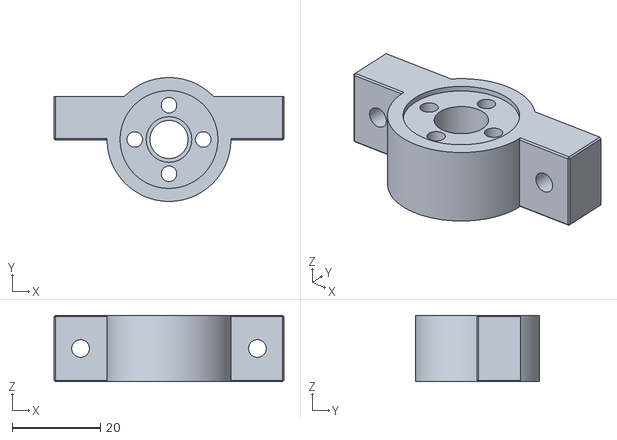
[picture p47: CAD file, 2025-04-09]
docs/3d/stl/t8.stl
52.0 x 28.0 x 15.0

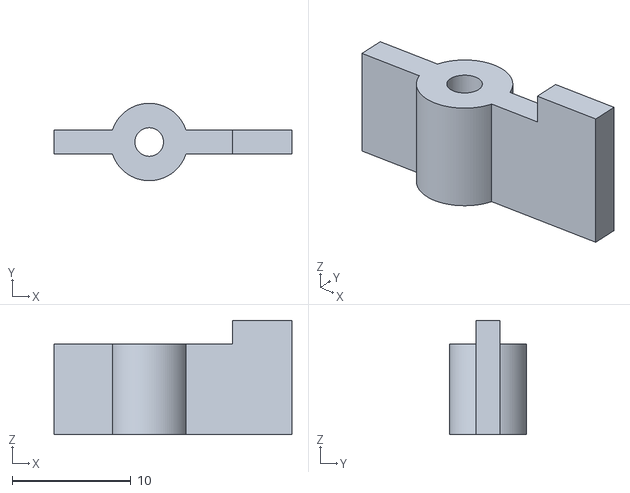
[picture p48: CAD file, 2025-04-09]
docs/3d/stl/button.stl
20.0 x 6.50 x 9.60

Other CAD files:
docs/3d/stl/plastic_tester.stl
docs/3d/stl/gear t60 m1.stl
docs/3d/probeta v2.f3d
docs/3d/stl/frame motor.stl

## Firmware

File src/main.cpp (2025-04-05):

/*
 Name:		tester
 Created:	23/01/2025 12:49:23
 Author:	buho29
*/

#include "Arduino.h"
#include <algorithm>

#include "HX711.h"

#include <NetworkManager.h>
#include <FileJsonManager.h>
#include <MotorController.h>
#include <ServerManager.h>

#include "data.h"
#include "TestAnalyzer.h"

// host name to mDNS, http://plastester.local
const char *hostName = "plastester";
// HX711 scale
const int LOADCELL_DOUT_PIN = 26;
const int LOADCELL_SCK_PIN = 25;
const float CALIBRATING_FACTOR = -2316138 / 44.34; // read/real kg
HX711 scale;

// motor
const uint8_t MOTOR_STEP_PIN = 32;
const uint8_t MOTOR_DIRECTION_PIN = 33;
const uint8_t ENDSTOP_PIN = 27;
MotorController motor(MOTOR_STEP_PIN, MOTOR_DIRECTION_PIN, ENDSTOP_PIN);

FileJsonManager fileManager;
ServerManager server;
NetworkManager network;
bool resetWifi = false;

// permanent app variables, see data.h
//		to save the variables in a json file
Config config;

//		current sencor
SensorItem currentSensor;
TestAnalyzer analyzer;

const uint8_t MAX_HISTORY = 20;
DataArray<MAX_HISTORY, HistoryItem> history;

// 			APP
//		print config json
void printJsonConfig()
{
	JsonDocument doc;
	String str;
	JsonObject obj = doc.to<JsonObject>();

	config.serializeItem(obj, false);
	serializeJsonPretty(doc, str);
	Serial.println(str.c_str());
}
//		print history json
void printJsonHistory()
{
	String str = history.serializeString();
	Serial.println(str.c_str());
}

//		return String in json format
String createJsonOption()
{
	// uint32_t c = millis();
	JsonDocument root;
	String str;

	JsonObject doc = root["config"].to<JsonObject>();
	config.serializeItem(doc, true);

	serializeJsonPretty(root, str);
	// Serial.printf("createJsonOption %d ms\n", millis() - c);
	// Serial.println(str.c_str());
	return str;
}
String createJsonSensors()
{
	//{"ss":{"d":77.10,"f":46.49}}
	return String("{\"ss\":{\"d\":") +
		   currentSensor.distance + ",\"f\":" +
		   currentSensor.force + "}}";
}
String createJsonHistory()
{
	JsonDocument root;
	String json;
	uint32_t c = millis();

	JsonArray doc = root["hystory"].to<JsonArray>();
	history.serializeData(doc);

	serializeJsonPretty(root, json);

	Serial.printf("printJsonFiles total %d ms\n", millis() - c);

	return json;
}
String createJsonResults(JsonArray &array)
{
	static DataArray<TestAnalyzer::MAX_RESULT, SensorItem> result;

	uint32_t c = millis();
	JsonDocument root;
	String json;

	JsonArray doc = root["results"].to<JsonArray>();

	for (JsonVariant v : array)
	{
		uint index = v.as<uint>();
		HistoryItem *item = history[index];
		if (item)
		{
			String path = String("/data") + item->pathData;

			JsonObject obj = doc.add<JsonObject>();
			obj["name"] = item->name;
			obj["date"] = item->date;
			obj["description"] = item->description;
			obj["avg_count"] = item->averageCount;
			obj["length"] = item->length;
			obj["area"] = item->area;

			if (fileManager.readJson(path.c_str(), &result))
			{
				JsonArray arr = obj["data"].to<JsonArray>();
				result.serializeData(arr);
				// Serial.printf("[%d] path:%s\n", index, path.c_str());
				// Serial.println(result.serializeString() + "\n");
			}
			//
		}
	}

	serializeJson(root, json); // Pretty

	Serial.printf("createJsonResults total %d ms\n", millis() - c);

	// Serial.println(json);

	return json;
}
String createJsonLastResult()
{
	uint32_t c = millis();
	JsonDocument root;
	String json;

	JsonArray doc = root["lastResult"].to<JsonArray>();
	analyzer.accumulated_data.serializeData(doc);

	serializeJson(root, json); // Pretty

	// Serial.printf("createJsonResults total %d ms\n", millis() - c);
	Serial.println(json);

	return json;
}

// primera contacto
void clientConnected(AsyncWebSocketClient *client)
{
	uint32_t c = millis();
	JsonDocument root;
	String json;

	JsonArray doc = root["history"].to<JsonArray>();
	history.serializeData(doc);

	serializeJsonPretty(root, json);
	server.send(json, client);

	//Serial.printf("sendHistory total %d ms\n", millis() - c);
}

// manage data results
void deleteResult(uint8_t index, AsyncWebSocketClient *client)
{
	HistoryItem *item = history[index];
	if (item)
	{
		String file = String("/data") + item->pathData;

		if (history.remove(item) && fileManager.deleteFile(file))
		{
			if (fileManager.writeJson("/data/results.json", &history))
			{
				server.sendMessage(ServerManager::GOOD, "result deleted", client);
				clientConnected(nullptr); // send all udpdate
				server.updateJsonFile();
			}
			else
				server.sendMessage(ServerManager::ERROR, "error write history file", client);
		}
		else
			server.sendMessage(ServerManager::ERROR, "error result not found file", client);
	}
	else
		server.sendMessage(ServerManager::ERROR, "error deleted not found result", client);
}
void saveResult(JsonObject &obj, AsyncWebSocketClient *client)
{
	if (obj["id"].is<uint8_t>() && 
		obj["desc"].is<const char *>() && 
		obj["area"].is<float>() && 
		obj["length"].is<float>() )
	{
		uint8_t index = obj["id"];
		HistoryItem *item = history[index];
		
		if (item)
		{
			strcpy(item->description, obj["desc"]);
			item->area = obj["area"];
			item->length = obj["length"];

			if (fileManager.writeJson("/data/results.json", &history))
			{
				server.sendMessage(ServerManager::GOOD, item->name + String(" saved"), client);
				clientConnected(nullptr); // send all udpdate;
			}
			else
				server.sendMessage(ServerManager::ERROR, "error write history file", client);
		}
		else
			server.sendMessage(ServerManager::ERROR, "error result not found file", client);
	}
	else
		server.sendMessage(ServerManager::ERROR, "error result not saved", client);
}
void renameResult(JsonObject &obj, AsyncWebSocketClient *client)
{
	if (obj["id"].is<uint8_t>() && obj["name"].is<const char *>())
	{
		uint8_t index = obj["id"];
		const char *name = obj["name"];

		HistoryItem *item = history[index];

		String p = String("/result/") + name + ".json";
		String file = "/data" + p;
		const char *path = p.c_str();

		if (item)
		{
			if (fileManager.exists(file))
			{
				server.sendMessage(ServerManager::ERROR, "the name already exists choose another", client);
			}
			else if (item->isValide(path, name, item->date, item->description))
			{
				String old = String("/data") + item->pathData;
				if (fileManager.renameFile(old.c_str(), file.c_str()))
				{
					strcpy(item->pathData, path);
					strcpy(item->name, name);
					if (fileManager.writeJson("/data/results.json", &history))
					{
						String path = String("/result/") + name;
						server.goTo(path.c_str(), client);
						server.sendMessage(ServerManager::GOOD, name + String(" renamed!"), client);
						// send all update;
						clientConnected(nullptr);
						server.updateJsonFile();
					}
					else
						server.sendMessage(ServerManager::ERROR, "error write history file", client);
				}
				else
					server.sendMessage(ServerManager::ERROR, "error rename file", client);
			}
			else
				server.sendMessage(ServerManager::ERROR, "error input data not is valid", client);
		}
		else
			server.sendMessage(ServerManager::ERROR, "error result not found file", client);
	}
	else
		server.sendMessage(ServerManager::ERROR, "error result bad parameter rename", client);
}
void newResult(JsonObject &obj, AsyncWebSocketClient *client)
{
	HistoryItem *item = history.getEmpty();

	if (!item)
	{
		server.sendMessage(ServerManager::ERROR, String("Only ") + history.maxSize + " items can be saved, please delete some", client);
		server.goTo("/history", client);
	}
	else if (analyzer.isEmpty())
	{
		server.sendMessage(ServerManager::WARN, " last result not found", client);
	}
	else if (
		obj["name"].is<const char *>() &&
		obj["desc"].is<const char *>() &&
		obj["date"].is<const char *>() &&
		obj["length"].is<float>() &&
		obj["area"].is<float>())
	{
		const char *name = obj["name"];
		const char *date = obj["date"];
		const char *description = obj["desc"];
		float length = obj["length"];
		float area = obj["area"];

		String p = String("/result/") + name + ".json";
		String file = "/data" + p;
		const char *path = p.c_str();

		if (fileManager.exists(file))
		{
			server.sendMessage(ServerManager::ERROR, "the name already exists choose another", client);
		}
		else if (item->isValide(path, name, date, description))
		{
			Serial.printf("new result %s %s\n", file.c_str(), path);
			//	save result
			// Serial.printf("%s\n", analyzer.accumulated_data.serializeString().c_str());
			if (fileManager.writeJson(file.c_str(), &analyzer.accumulated_data))
			{
				item->set(path, name, date, description, length, area);
				history.push(item);
				if (fileManager.writeJson("/data/results.json", &history))
				{
					String path = String("/result/") + name;
					server.goTo(path.c_str(), client);
					server.sendMessage(ServerManager::GOOD, name + String(" created!"), client);
					// TODO crear cmd puto vago
					//clear result in client 
					analyzer.clear();
					server.send(createJsonLastResult(), client);
					// send all update;
					clientConnected(nullptr);
					server.updateJsonFile();
				}
				else
					server.sendMessage(ServerManager::ERROR, "error write history file", client);
			}
			else
				server.sendMessage(ServerManager::ERROR, "error write result file", client);
		}
		else
			server.sendMessage(ServerManager::ERROR, "error input data not is valid", client);
	}
}

enum Step
{
	STOP = 0,
	START = 1,
	MEASURING = 2, // measuring
};
Step testStep = STOP;
enum State
{
	EMPTY = 0,
	RUNHOME = 1,
	TESTRUN = 2
};
State state = EMPTY;
void setupSensors()
{
	scale.begin(LOADCELL_DOUT_PIN, LOADCELL_SCK_PIN);
	scale.set_scale(CALIBRATING_FACTOR);
	scale.tare(80);
}
void readSensors()
{
	if (scale.is_ready())
	{
		currentSensor.set(
			motor.getPosition(),
			scale.get_units(1));
	}
	else
		currentSensor.distance = motor.getPosition();
}
void updateSensors()
{
	static uint32_t c = 0;
	if (millis() - c > 200)
	{
		// int t = micros();
		if (state != State::TESTRUN)
			readSensors();

		server.send(createJsonSensors());
		c = millis();
		// Serial.printf("readsensor %.2f\n",(micros()-t)/1000.0);
	}
}

// validation user action
bool limitChecked = false;
bool isLimitChecked(AsyncWebSocketClient *client)
{
	if (!limitChecked)
	{
		server.sendPopup("Warn",
						 "Attention!,<br>The limit will be checked.",
						 "{\"checkLimit\":1}", client);
		return false;
	}
	return true;
}
bool isRunning(AsyncWebSocketClient *client)
{
	if (motor.isRunning())
	{
		server.sendMessage(ServerManager::ERROR, "First stop motor", client);
		return true;
	}
	return false;
}
bool isTestRunning(AsyncWebSocketClient *client)
{
	if (state == TESTRUN)
	{
		server.sendMessage(ServerManager::ERROR, "The test is running, please stop it or wait.", client);
		return true;
	}
	return false;
}
bool isHomePos(AsyncWebSocketClient *client)
{
	if (motor.getPosition() != 0)
	{
		server.sendPopup("Warn",
						 "Attention!,<br>The motor is not in the home position.",
						 "{\"sethome\":1}", client);
		return false;
	}
	return true;
}

void defaultConfigMotor()
{
	// 200steps/revolution   stepping 1/8 reduction 60:10 screw pitch 2mm
	const float steps_mm = 200 * config.micro_step * 6 / config.screw_pitch;
	motor.setConfigMotor(steps_mm, config.speed, config.acc_desc, config.invert_motor);
	motor.setConfigHome(config.home_pos, config.max_travel);
}
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

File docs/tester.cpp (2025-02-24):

#include <Arduino.h>

#include <lvgl.h>
#include <TFT_eSPI.h>
#include "HX711.h"
#include <ESP_FlexyStepper.h>
#include "Adafruit_VL53L0X.h"

//////////////// hardware /////////////////
// screen
TFT_eSPI tft = TFT_eSPI(); /* TFT instance */
/*screen resolution*/
const uint32_t screenWidth = 320;
const uint32_t screenHeight = 240;

lv_disp_draw_buf_t draw_buf;
lv_color_t buf[screenWidth * 10];

//bascula:
HX711 scale;
const uint8_t HX711_dout = 26;  //mcu > HX711 dout pin
const uint8_t HX711_sck = 25;   //mcu > HX711 sck pin

// motor
const uint8_t MOTOR_STEP_PIN = 32;
const uint8_t MOTOR_DIRECTION_PIN = 33;
ESP_FlexyStepper stepper;

// "medidor laser"
Adafruit_VL53L0X lox;  // = Adafruit_VL53L0X();

////////////  app   ////////////
// limite de maquina (mm)
const uint8_t MAX_LIMIT = 220;
const uint8_t MIN_LIMIT = 45;

const uint8_t MAX_WEIGHT = 50;

float weight_sensor = 0.0;
int distance_sensor = 50;
float rel_dist_to_move = 0.5;
float home_pos = 78.0;
uint32_t fps;
//test
const uint8_t res_data_len = 200;
lv_coord_t res_data[res_data_len];

uint8_t test_step = 0, test_dist = 5;
float test_max_weight, test_zero_pos, test_diff_pos, test_trigger_weigth;
bool test_stopping;
uint8_t test_saved_index;

////////////////   UI   ////////////

lv_obj_t *tiles;
lv_obj_t *fps_label;

lv_obj_t *tileTest;
lv_obj_t *test_weight_label, *test_weight1_label;
lv_obj_t *test_dist_label, *test_pos_label;
lv_obj_t *test_spin_trigger, *test_spin_dist;

lv_obj_t *tileResult;
lv_obj_t *res_chart, *res_label;
lv_chart_series_t *res_series;
lv_chart_cursor_t *res_cursor;

lv_obj_t *tileWeight;
lv_obj_t *wei_meter, *wei_weight_label;
lv_meter_indicator_t *wei_indicator;

lv_obj_t *tileRelative;
lv_obj_t *rel_weight_label, *rel_position_label;

lv_obj_t *tileAbsolute;
lv_obj_t *abs_spin_dist, *abs_spin_speed;
lv_obj_t *abs_spin_acc;
lv_obj_t *abs_weight_label, *abs_position_label;

lv_style_t st_cont, st_font_large;


/////////////// arduino  /////////////////

void setup() {
  Serial.begin(115200);

  setupTft();
  setupSensors();
  setupMotor();

  mainView();
}

void loop() {
  //int ti = millis();

  readSensors();

  //limit
  if (isLimit()) stepper.setTargetPositionToStop();

  calcFps(1);

  update();

  lv_timer_handler(); /* let the GUI do its work */

  //ti = millis() - ti;
  //if (ti > 100) Serial.printf("%d ms \n", ti);
}

/////////////// app  ///////////////////

void mainView() {
  init_styles();

  tiles = lv_tileview_create(lv_scr_act());

  tileTest = lv_tileview_add_tile(tiles, 0, 0, LV_DIR_BOTTOM | LV_DIR_RIGHT);
  tileResult = lv_tileview_add_tile(tiles, 1, 0, LV_DIR_LEFT);

  tileAbsolute = lv_tileview_add_tile(tiles, 0, 1, LV_DIR_BOTTOM | LV_DIR_RIGHT | LV_DIR_TOP);
  tileRelative = lv_tileview_add_tile(tiles, 1, 1, LV_DIR_LEFT);
  tileWeight = lv_tileview_add_tile(tiles, 0, 2, LV_DIR_TOP);

  makeTileTest(tileTest);
  makeTileAbsolute(tileAbsolute);
  makeTileRelative(tileRelative);
  makeTileWeight(tileWeight);
  makeTileResult(tileResult);

  lv_obj_set_tile(tiles, tileTest, LV_ANIM_OFF);

  fps_label = lv_label_create(lv_scr_act());
  lv_obj_align(fps_label, LV_ALIGN_TOP_RIGHT, -15, 10);
}
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
